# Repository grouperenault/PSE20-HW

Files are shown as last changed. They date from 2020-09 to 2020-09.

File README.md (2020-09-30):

# PSE20-HW

All the files in this directory (and its subdirectories) are subject to
the CERN-OHL-S v2 licence.

Copyright Renault SAS 2020.

This source describes Open Hardware and is licensed under the CERN-OHL-S v2.
You may redistribute and modify this documentation and make products
using it under the terms of the CERN-OHL-S v2 (https:/cern.ch/cern-ohl).

This documentation is distributed WITHOUT ANY EXPRESS OR IMPLIED
WARRANTY, INCLUDING OF MERCHANTABILITY, SATISFACTORY QUALITY
AND FITNESS FOR A PARTICULAR PURPOSE. Please see the CERN-OHL-S v2
for applicable conditions.

This repository contains the Design files for the CAD and Electronic elements of the PSE20-HW project.

For a detailed description of the ELECSYR syringe pump, please refer to [the documentation section](documentation/).

Two stacked ELECSYR units

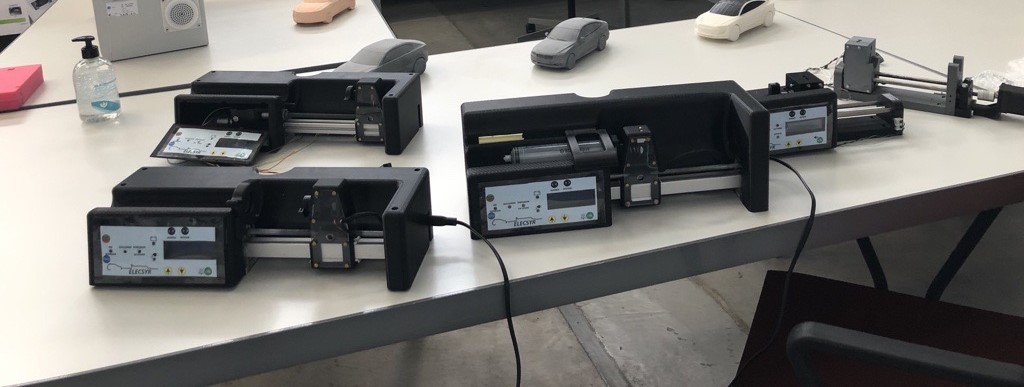
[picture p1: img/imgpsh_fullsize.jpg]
Early ELECSYR prototypes


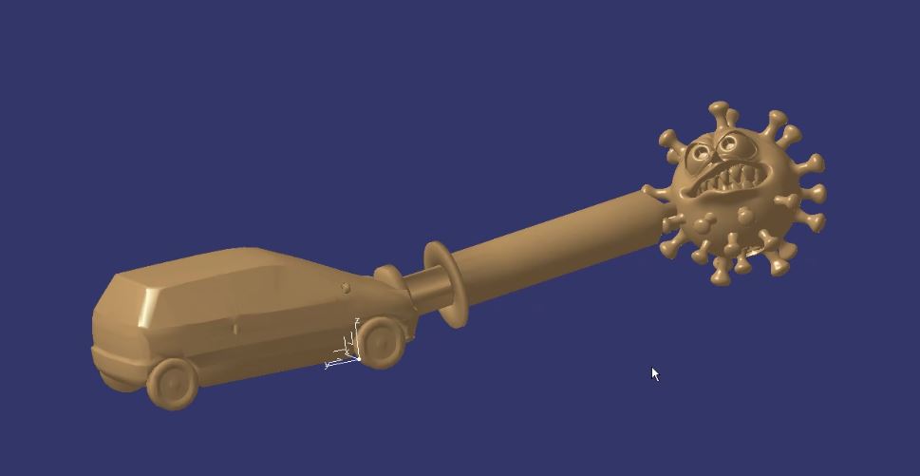
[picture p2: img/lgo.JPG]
Project Logo


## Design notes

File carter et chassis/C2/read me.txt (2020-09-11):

in this directory, you will find 3D data about C2 housing
data about other components (chassis, cutting plastic parts etc) are in C1 directory

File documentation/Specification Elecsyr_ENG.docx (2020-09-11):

Functionnal and technical description of ElecSyr, Electrical Syringe Pump

Contents

# 1. Historical

Name | Modifications | Version | Date
Sébastien LAURENT | Creation | 0.1 | 27/06/2020
Sébastien LAURENT | English translation | 0.2 | 11/08/2020

# 2. Documents

## 2.1. Generic documents

Subject | Document Name | Reference | Version
Sécurité performances pompes perfusion | Exigences particulières pour la sécurité de base et les performances essentielles des pompes et régulateurs de perfusion | IEC 60601-2 24
Sécurité & performance appareils médicaux | Exigences générales pour la sécurité de base et les performances essentielles des appareils électro-médicaux | IEC 60601-1
CEM des appareils médicaux | Exigences générales pour la sécurité de base et les performances essentielles – Norme collatérale: Perturbations électromagnétiques – Exigences et essais | IEC 60601-1-2

## 2.2. Specific documents

Subject | Document Name | Reference | Version | Comments
functional Test report | Rapport de test AGEPS | | | On demand only

# 3. Abbréviations and définitions

## 3.1. Definitions

## 3.2. Abbréviations

PSE | : | Electrical Syringe Pump (In french, Pousse Seringue Electrique)

# 4. Purpose

The purpose of this document is to describe functionality and technical points of the ElecSyr Electrical syringe pump.

## 4.1. Context

Dans le contexte de la pandémie actuelle, le pousse seringue électrique, PSE, permet d’injecter des médicaments selon plusieurs modes.

En réanimation, les patients atteints du COVID 19 nécessitent l’utilisation de 5 à 7 PSE afin de pouvoir injecter les médicaments différents.

Notre étude porte sur un PSE basique, nommé ElecSyr, permettant de répondre à l’urgence.

Ce pousse-seringues, bien que conçu pendant le pic de la pandémie, peut répondre à d’autres besoins.

Dans notre étude, nous prenons en compte les modes de fonctionnement suivant

- Continu : injection en continu d’un produit
- Bolus : injection ponctuelle à débit plus élevé. Le mode Bolus est un complément au mode continu. C’est-à-dire, que l’injection de la drogue etant en mode continu le praticien peut venir soulager le patient en lui injectant une dose plus forte ponctuellement

In the context of the current pandemic, the electric syringe pump, PSE, allows the injection of drugs in several ways.

In intensive care, patients with COVID 19 require the use of 5 to 7 PSE in order to be able to inject needed drugs.

Our study focuses on a basic PSE, called ElecSyr, to respond to the emergency.

This syringe pump, although designed during the peak of the pandemic, can meet other needs.

In our study, we take into account the following modes of operation

- Continuous injection of a product
- Bolus: a higher-flow one-off injection. The Bolus mode is a complement to the continuous mode. That is, that the injection of the drug being in continuous mode the practitioner can come to relieve the patient by injecting a higher dose punctually

# 5. global description

## 5.1. Technical features

ElecSyr is composed as folowing :

Main features are :

Built-in features | Values
Flow | Min: 1 ml/h and max 1200ml/h
Step-by-step setting | 0,1ml/h
Power
220V - 60Hz
Internal backup battery | More than 1 hour autonomy (tbc)
Mode
Continuous | Fixed flow adjusted by user
Bolus | 500ml/h for speed (this value may be change in configuration mode) Durin bolus, injected volume is shown on screen
Alert
End Course Av | LED alert - Sound - message
End Race 10% | LED alert - Sound - message
Detection Occlusion | LED alert - Sound - message
sector/battery | LED battery / LED Sector
device failure (internal check) | message - Sound
Syringes
Possible adjustments | InternalTable of 6: default BD platispak 50ml Luer Lock
Fixation
on set
onvertical colonn

## 5.2. Human Machine Interface

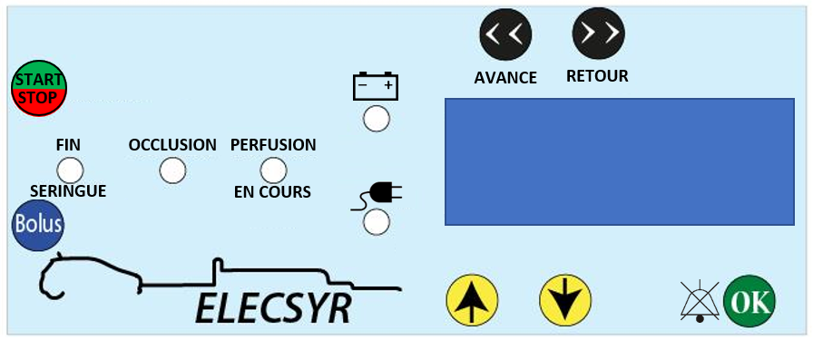
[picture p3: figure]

The HMI consists of:

- Start/stop button: used to start or stop the infusion
- Bolus button: used to launch the Bolus function
- Fast Forward button: used to move at high speed the trolley to meet the syringe
- Fast reward button: used to move in reverse speed the trolley.
- OK button: allows you to make and validate the settings (syringe choice, flow choice), to mute the sound of the alarms
- Button up: When settings it allows you to increment the flow values and choose the syringe
- Down button: When settings it allows you to decrement the flow values and choose the syringe
- Led End syringe: used to indicate 10% end of injection and end of injection
- Led Occlusion: It indicates an occlusion
- Led Perfusion in progress: green indicator indicating an infusion in progress
- Led Bat OK: Battery status indicator
- Led Sector OK: Industry Status Indicator
- A Buzzer makes sounds during different alarms
- An LCD with 2 lines – 16 characters allows you to see all the necessary information

# 6. Models

Following different tests done and exchanges with medical people, different models were developed to take into account the constraints of hospitals (stackable, waterproof, syringe fixing points), functional constraints (spring or electronic overpressure sensor) and production tools (electronic board with through-hole technology or SMD, 3D printing and cutting).

Consequently, there are 10 possible versions of ElecSyr

Assembly | Housing | mecanism | PCB | Software | Pressure sensor | comments
1 | C1 | 2 | Through hole | 1 | Spring | Checked by AGEPS
2 | C1 | 2 | Through hole | 2 | Electronic (Tyco) | Checked by AGEPS
3 | C1 | 2 | SMD | 1 | Spring | Equal to Assembly 1
4 | C1 | 2 | SMD | 2 | Electronic (Tyco) | Checked by AGEPS
5 | C2 | 2 | Through hole | 1 | Spring | Equal to Assembly 1
6 | C2 | 2 | Through hole | 2 | Electronic (Tyco) | Equal to Assembly 2
7 | C2 | 2 | SMD | 1 | Spring | Equal to Assembly 1
8 | C2 | 2 | SMD | 2 | Electronic (Tyco) | Equal to Assembly 4
9 | C3 | 2 | SMD with reduced size | 1 | Spring | Digital version only
10 | C3 | 2 | SMD with reduced size | 2 | Electronic (Tyco) | Digital version only

Housing 1 : easy to stack

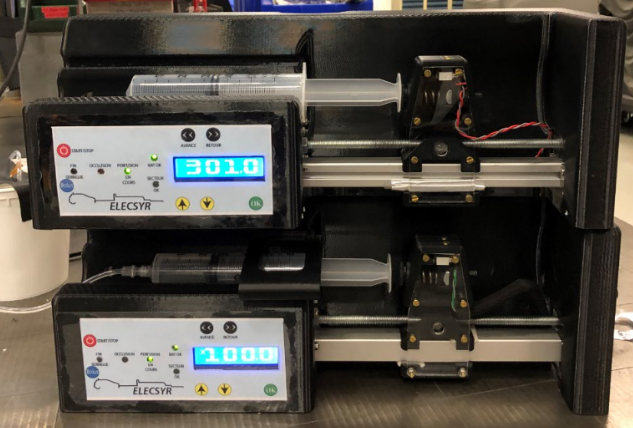
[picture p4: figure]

housing 2 : reduced height, stackable by small rods to put inside hole

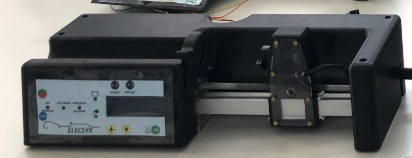
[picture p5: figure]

housing 3 : same as 2, with smaller length and width (-30mm)

Electronic board : through hole technology with Arduino board

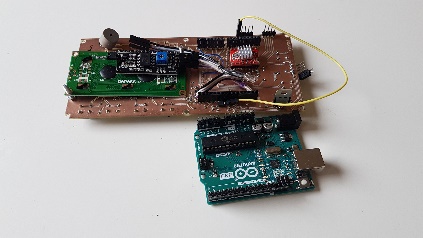
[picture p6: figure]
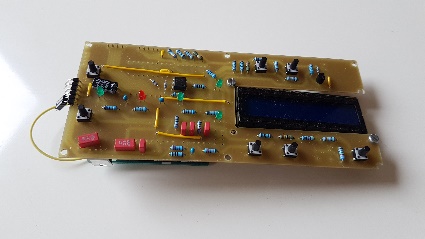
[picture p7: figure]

Electronic board: SMD technology (atmel IC is directly integrated on the board – no Arduino board)

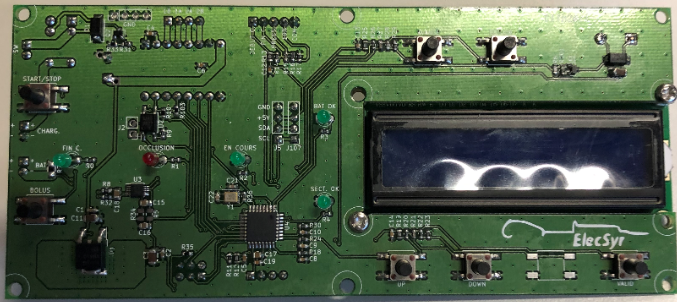
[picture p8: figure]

Spring pressure sensor

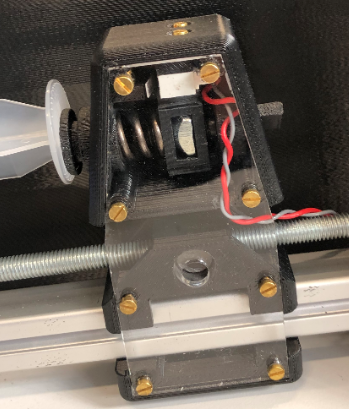
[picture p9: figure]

Electronic pressure sensor from TE Connectivty. The FX29K0-100B-0025-L was used instead of spring and mechanical detection. This systems allows to adjust with more accuracy pressure level It also helps in end of course detection and about syrnge positioning. With this sensor we are able to integrate an automatic fast positioning till syringe detection.

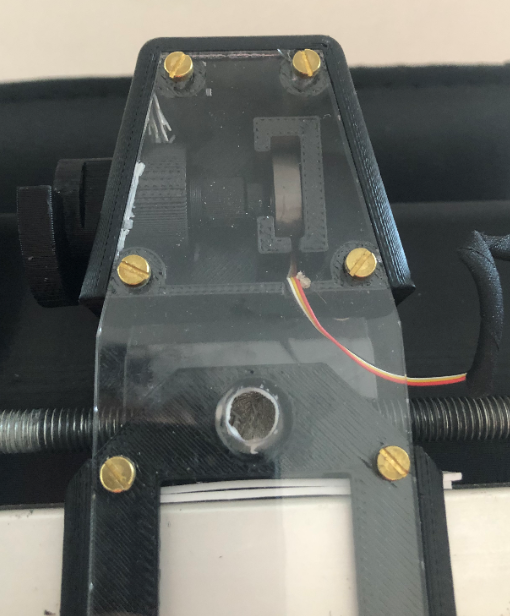
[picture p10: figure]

# 7. Functional descrption

## 7.1. State flow

## 7.2. Initialisation

When power is set on , the device starts and makes internal checks. If ok, it initiates feed monitoring and puts itself in a state of waiting.

## 7.3. Surveillance alimentation

The system checks states of main power supply and battery.

## 7.4. Etat d’attente

In that mode, you can :

- Choice and validate the syringe by using Up & Down button and OK button

Syringe 1 corresponds to the plastipak luer lock 50ml BD

- Set the flow

Flow may be adjusted by UP and DOWN buttons and each number is validated by pressing OK button

## 7.5. Distribution

Continuous:

Once the syringe and flow are validated, the Start/Stop button tap allows you to launch/stop the infusion.

At any time, if an infusion is in progress, the start/stop button stops the current infusion

Bolus :

A first push allows you to enter in Bolus function

A second continuous push launches the bolus function: the flow that appears on the screen corresponds to the additional quantity injected via the bolus function.

When the button is released, ElecSyr returns to its previous state (continuous infusion or waiting)

This mode is only available during continuous injection or waiting mode

## 7.6. Avance rapide

By pushing it, you can move quickly the trolley in direct way

If Elecsyr is equipped with an electronic pressure sensor, this function is made automatically by a push.

If Elecsyr is equipped with mechanical pressure detection, a continue push is necessary to move the trolley.

## 7.7. Retour rapide

By pushing it, you can move quickly the trolley in reverse way

Specification Elecsyr_ENG revision : 0.1 12/27 Confidential C

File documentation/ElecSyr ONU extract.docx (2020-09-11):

ElecSyr, made by Renault

# Document description

This document is an extract of project call from ONU.

ElecSyr was a candidate but didn’t win any award.

# Project description

At the start of the pandemic, a Renault team was formed to design a "basic" automatic electric syringe pump to meet the needs of hospitals. As part of the treatment of COVID, each patient requires between 5 and 7 syringe pumps. There was a high risk of supply disruption. We got closer to the nursing staff (nurse and doctors), in order to understand the basic functions of a syringe pump. ElecSyr allows continuous and / or pulsed injection of a drug by infusion. The flow rate is adjustable, min value: 2ml / h. Different types of syringes are accepted with default BD plastipak Luerlock 50ml. ElecSyr is made from simple components:

- 3D printed parts

- cut pieces

- electronic board with Arduino board (or only Atmel chip)

- Stepper motor Nema 17

ElecSyr has a cost price around 200€ without any negociation and in very small quantity. It is easy to assemble

# Added Value against COVID

ElecSyr makes it easier to manage, through automation, the administration of continuous medication. It is easily reprogrammable to add new syringe models and enrich its functionalities. ElecSyr is simple to manufacture and its cost price is very low compared to existing product on the market. Usable in the context of the current pandemic, it may subsequently be used for the treatment of other pathologies. hospitals that do not currently have a syringe pump because of the high cost, it is also an opportunity to get one.

# Innovative content of the proposal

the innovation consists of the simple, frugal realization of the electric syringe pump. it is a response to the current emergency. Its modular design makes it possible to take into account the means of production available: laser cutting, 3D printing, 3 housing solutions (stackable, reduced height, reduced bulk), 3 electronic boards depending on tools and skills (SMD or through components), spring or electronic pressure sensor ; by these choices, it is possible to assembly 10 different ElecSyr syringe pumps.

# Impact on economic, social, and environmental sustainability

- design from basic components

- Simple assembly

- simple realization

- scalable and adaptable: the software and electronics can easily be upgraded to consider current and future local needs

- repairability

- Economic

- no environmental impact

# Potential benefits for developing countries

- provide material meeting the basics of a syringe pump at a much lower cost than an existing product - ease of supply of parts, manufacturing and assembly - the software, easily upgradeable, can integrate local constraints (type of syringes, flow ranges, new features)

- simple assembly, repairable

- few components

# Development stage

3 phases of prototypes produced: - a first in 3D printing to verify the technical choices - a second integrating the constraints of the bichat hospital (Paris): waterproofing, fixing, stacking, alerts, messages for nursing staff These second prototypes were tested in hospitals in Paris (functional) - a third version integrating test feedback, more compact with SMD electronic components and electronic pressure sensor - EMC tests planned, to be carried out To do : - optimization on trolley sensor mounting. - Assembly to be finalized taking into account local functional and assembly needs (3D tool) need in terms of Manufacturing, assembly software development for update and complement. production of electronic cards

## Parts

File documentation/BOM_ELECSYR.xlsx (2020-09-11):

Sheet: SMD board
Id | Ref | Empreinte | Qté | Désignation | Fournisseur | ref
1 | R7 | R_1206_3216Metric_Shunt | 1 | 0.1R | RS | 566-058
2 | SW3A1,SW2A1,SW2B1,SW2C1,SW3C2,SW3D2,SW3B1 | SW_SPST_B3S-1000 | 7 | Switch façade | RS | 718-2459
3 | BT1,J1,SW1A101 | PinHeader_1x02_P2.54mm_Vertical | 3 | embase JST XH 2 pin | RS | 820-1554
4 | J3 | PinHeader_1x04_P2.54mm_Vertical | 1 | Pin header 4 pin | RS
5 | M1 | PinHeader_1x04_P2.54mm_Vertical | 1 | embase JST XH 4 pin | RS | 820-1551
6 | J103 | PinHeader_1x05_P2.54mm_Vertical | 1 | embase JST XH 5 pin | RS | 820-1560
7 | A2 | Pololu_Breakout-16_15.2x20.3mm | 1 | Pololu_Breakout_A4988 | Reprap
8 | C8,C10,C1,C2,C9 | C_0603_1608Metric | 5 | 47n | RS | 652-0162
9 | R18,R30,R24 | C_0603_1608Metric | 3 | 22k | RS | 679-0005
10 | C6,C4,C5,C12,C13,C14,C19 | C_0603_1608Metric | 7 | 100n | RS | 133-5658
11 | U1 | TO-252-2 | 1 | NCP1117-1.5_TO252 | RS | 516-5871
12 | U2 | SO-4_4.4x3.6mm_P2.54mm | 1 | LTV-357T | RS | 691-2088
13 | REF** | LCD1602_2 | 1 | LCD 16x02 I2C | amazon | https://www.amazon.fr/gp/product/B07PGZ9B51/ref=ppx_yo_dt_b_asin_title_o03_s01?ie=UTF8&psc=1
14 | D4,D6,D9,D10 | LED_D3.0mm | 4 | Led VERTE | RS | 180-8502
15 | D5 | LED_D3.0mm | 1 | Led ROUGE | RS | 178-0909
16 | R0,R1,R2,R3,R4,R9 | R_0603_1608Metric | 6 | 680 | RS | 820-6887
17 | R6,R11,R31 | R_0603_1608Metric | 3 | 2.2k | RS | 820-6824
18 | R12,R13,R19,R25 | R_0603_1608Metric | 4 | 1k | RS | 223-0427
19 | R8,R14,R20,R26,R32 | R_0603_1608Metric | 5 | 249 | RS | 679-0037
20 | R15,R21,R27 | R_0603_1608Metric | 3 | 412 | RS | 122-8862
21 | R16,R22,R28 | R_0603_1608Metric | 3 | 825 | RS | 679-0728
22 | R17,R23,R29 | R_0603_1608Metric | 3 | 2490 | RS | 679-0147
23 | Q1,Q2 | SOT-23 | 2 | BC817 | RS | 216-9410
24 | C3,C11,C23 | C_1206_3216Metric | 3 | 10u | RS | 802-9977
25 | R10,R101,R103,R33,R35 | R_0603_1608Metric | 5 | 10k | RS | 678-9667
26 | LS1 | Buzzer_12x9.5RM7.6 | 1 | Buzzer | RS | 771-6967
27 | D2,D1 | D_SMA | 2 | S1G | RS | 761-3723
28 | C7 | CP_Radial_D10.0mm_P5.00mm_P7.50mm_H16mm | 1 | 470u | RS | 315-0574
29 | C15,C16,C17,C18 | C_0805_2012Metric | 4 | 1u | RS | 133-5653
30 | C21,C22 | C_0603_1608Metric | 2 | 12p (value depend of Y1) | RS | 652-0926
31 | J4 | PinHeader_2x03_P2.54mm_Vertical | 1 | ICSP | RS
32 | K1 | Relay_SPDT_Omron_G5V-1 | 1 | G5V-1 9 | RS | 683-9255
33 | R5,R34 | R_0805_2012Metric | 2 | MMZ2012Y152B | RS | 604-2022
34 | R36 | R_0603_1608Metric | 1 | 1M | RS | 213-2676
35 | U3 | TSSOP-10_3x3mm_P0.5mm | 1 | ADS1115IDGS | RS | 709-4544
36 | U4 | TQFP-32_7x7mm_P0.8mm | 1 | ATMega328P-AU | RS | 131-0271
37 | Y1 | Crystal_SMD_3225-4Pin_3.2x2.5mm | 1 | 16MHz | RS | 775-3736
38 |  |  | 1 | Porte clip JST XH 5 pin | RS | 820-1627
39 |  |  | 1 | Porte clip JST XH 4 pin | RS | 820-1618
40 |  |  | 3 | Porte clip JST XH 2 pin | RS | 820-1611
41 |  |  | 15 | Clip JST XH | RS | 820-1529
44 |  |  | 1 | microrupteur ss lamelle | RS | 804-6253
45 |  |  | 2 | microrupteur lamelle | RS | 804-6262

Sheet: Mechanical parts
ss éléments |  | nombre
Chariot | chariot inférieur | 1 | 3D
 | patins teflon | 2
 | ecrou tranversal M8 | 1
 | chariot supérieur | 1 | 3D
 | pousse-piston | 1 | 3D
 | escargot piston | 1 | 3D
 | axe maintien escargot | 1
 | plaque latérale | 2
 | tige appui micro switch | 1
 | vis appui patin M2*8 | 4
 | vis M3*36 | 8
 | ecrou M3 | 8
 | rondelle plate M3 | 8
Mécanisme | profilé alu 20*20*250 | 1
 | roulement 608ZZ | 1 | reprap
 | tige filetée M8 | 1
 | support moteur | 1 | 3D
 | coupleur 5mm*8mm | 1 | reprap
 | moteur Nema 17 0,48Nm | 1 | reprap
extérieur | carter | 1
 | support facade | 1
 | vis fixation façade M2 *5 | 6
 | vis fixation carter M2*8 | 10
chassis | socle | 1
 | support mecanisme G | 1
 | support mecanisme D | 1
 | flasque arret roulement | 1
 | flasque maintien chargeur | 2
 | Arret X chargeur | 1
 | flasque maintien batterie | 2

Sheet: EE parts
 |  |  | Supplier | Reference
 | PCB CMS | 1 | CIF
 | A4988 - Pilote de moteur pas à pas Stepstick | 1 | reprap
 | Câble pour NEMA 17 de 20cm | 1 | reprap
 | Nema 17 | 1 | reprap
 | ventilateur (Not used) | 0 | reprap
 | coupleur 5*8 | 1 | reprap
 | LCD 2*16 | 1 | ?
cablage | cablage interne |  | internal team
 | Chargeur de batterie Mascot Pack batterie Lithium-Ion | 1 | RS | 463-1181
 | Bloc batterie rechargeable Ansmann Lithium-Ion 7.4V 2.6Ah x 2 | 1 | RS | 776-0857
 | cable secteur | 1 | RS | 873-0709
 | Interrupteur à bascule Rouge bipolaire On-Off lumineux IP44 | 1 | RS | 377-9759
 | Electronic pressure sensor | 1 | TE connectivity | FX 29

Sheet: through hole board
Id | Référence | Boitier | Quantité | Désignation | Fournisseur | ref
1 | A2 | Pololu_Breakout-16_15.2x20.3mm | 1 | Pololu_Breakout_A4988 | Amazon/
2 | U1 | TO-220-3_Vertical | 1 | LM7805_TO220 | RS | 298-8508
3 | U2 | DIP-6_W7.62mm | 1 | 4N35 | RS | 699-8155
4 | D4 | LED_D3.0mm | 1 | Fin_course VERTE | RS | 180-8502
5 | D5 | LED_D3.0mm | 1 | Occlusion ROUGE | RS | 178-0909
6 | D6 | LED_D3.0mm | 1 | PERF EN COURS VERT | RS | 180-8502
7 | D9 | LED_D3.0mm | 1 | BAT OK ROUGE | RS | 178-0909
8 | D10,D11 | LED_D3.0mm | 2 | LED verte | RS | 180-8502
9 | SW2A1 | SW_PUSH_6mm_H9.5mm | 1 | UP | RS | 479-1435
10 | SW2B1 | SW_PUSH_6mm_H9.5mm | 1 | DOWN | RS | 479-1435
11 | SW2C1 | SW_PUSH_6mm_H9.5mm | 1 | VALID | RS | 479-1435
12 | SW3A1 | SW_PUSH_6mm_H9.5mm | 1 | StartStop | RS | 479-1435
13 | SW3B1 | SW_PUSH_6mm_H9.5mm | 1 | BOLUS | RS | 479-1435
14 | SW2D1 | SW_PUSH_6mm_H9.5mm | 1 | Avance | RS | 479-1435
15 | SW3C2 | SW_PUSH_6mm_H9.5mm | 1 | RETOUR | RS | 479-1435
16 | SW3D2 | SW_PUSH_6mm_H9.5mm | 1 | RESERVE1 | RS | 479-1435
17 | Q1 | TO-92 | 1 | BC337 | RS | 671-1116
18 | A1 | Arduino_UNO_R3 | 1 | Arduino_UNO_R3 | RS | 715-4081
19 | R0,R1,R2,R3,R4,R6,R8 | R_Axial_DIN0204_L3.6mm_D1.6mm_P5.08mm_Horizontal | 7 | 680 | RS | 506-5024
20 | R5 | R_Axial_DIN0204_L3.6mm_D1.6mm_P5.08mm_Horizontal | 1 | 100 | RS | 477-7681
21 | R7,R10,R101 | R_Axial_DIN0204_L3.6mm_D1.6mm_P5.08mm_Horizontal | 3 | 10k | RS | 491-1645
22 | R9 | R_Axial_DIN0204_L3.6mm_D1.6mm_P5.08mm_Horizontal | 1 | 300 | RS | 683-4196
23 | R11 | R_Axial_DIN0204_L3.6mm_D1.6mm_P5.08mm_Horizontal | 1 | 2.2k | RS | 506-5096
24 | R12 | R_Axial_DIN0204_L3.6mm_D1.6mm_P5.08mm_Horizontal | 1 | 1k | RS | 683-3165
25 | R13,R19,R25 | R_Axial_DIN0204_L3.6mm_D1.6mm_P5.08mm_Horizontal | 3 | 1ko | RS | 683-3165
26 | R14,R20,R26 | R_Axial_DIN0204_L3.6mm_D1.6mm_P5.08mm_Horizontal | 3 | 249 | RS | 477-7798
27 | R15,R21,R27 | R_Axial_DIN0204_L3.6mm_D1.6mm_P5.08mm_Horizontal | 3 | 412 | RS | 683-3682
28 | R16,R22,R28 | R_Axial_DIN0204_L3.6mm_D1.6mm_P5.08mm_Horizontal | 3 | 825 | RS | 477-7912
29 | R17,R23,R29 | R_Axial_DIN0204_L3.6mm_D1.6mm_P5.08mm_Horizontal | 3 | 2490 | RS | 477-8038
30 | R18,R24,R30 | R_Axial_DIN0204_L3.6mm_D1.6mm_P5.08mm_Horizontal | 3 | 22k | RS | 506-5349
31 | R102 | R_Axial_DIN0204_L3.6mm_D1.6mm_P5.08mm_Horizontal | 1 | 1M | RS | 477-8662
32 | BT1 | PinHeader_1x02_P2.54mm_Vertical | 1 | Battery_Cell | RS | 251-8086
33 | J1 | PinHeader_1x02_P2.54mm_Vertical | 1 | Entree_chargeur | RS | 251-8086
34 | J5,depart masse,moteur pàp | PinHeader_1x04_P2.54mm_Vertical | 2 | Ecran_I2C | RS | 251-8115
35 | J103, | PinHeader_1x05_P2.54mm_Vertical | 2 | Conn_01x05_Male | RS | 251-8121
36 | J107 | PinHeader_1x04_P2.54mm_Vertical | 1 | Pression_I2C | RS | 251-8115
37 | LS1 | PinHeader_1x02_P2.54mm_Vertical | 1 | Speaker | RS | 251-8086
38 | C1,C3 | C_Disc_D3.0mm_W2.0mm_P2.50mm | 3 | 470n | RS | 118-016
39 | C4,C5,C6 | C_Disc_D3.0mm_W2.0mm_P2.50mm | 3 | 100n | RS | 115-023
40 | C7 | CP_Radial_D4.0mm_P2.00mm | 1 | 100u | RS | 711-1090
41 | C2,C8,C9,C10 | C_Disc_D3.0mm_W2.0mm_P2.50mm | 3 | 47n | RS | 115-001
42 | J2 | PinHeader_1x02_P2.54mm_Vertical | 1 | shunt Opto | RS | 251-8086
43 | J4 | PinHeader_1x02_P2.54mm_Vertical | 1 | shunt 5V Arduino | RS | 251-8086
44 |  | carte cuivre nu 160*100*1,6 | 1 |  | RS | 219-2123
 |  | Chargeur batterie | 1 |  | RS | 463-1181
 |  | Batterie | 1 |  | RS | 776-0857
 |  | HP (speaker) | 1 |  | RS | 771-6982
 |  | Ecran_I2C | 1 |  | Amazon/
 |  | Stepper Nema17 - 1,7A - 0.45Nm | 1 | 1.8° | RS | 535-0489
 |  | switch fin de course | 1 |  | RS | 804-6262
 |  | switch début de course | 1 |  | RS | 804-6262
 |  | switch reste 10% | 1 |  | RS | 804-6253
 |  | switch occlusion | 1 |  | RS | 804-6262
 |  | inter On/Off | 1 |  | RS | 377-9759
 |  | gaine thermo | 1 |  | RS | 700-4620
 |  | pin header femelle pour raccord | 1 |  | RS | 251-8171
 |  | pin header male/male | 4 |  | RS | 251-8339
 |  | pin header femelle pour raccord | 4 |  | RS | 251-8171
 |  | fraise 0,1mm | 5 |  | RS | 382-002
 |  | MANQUE COUPLEUR 4*8
 |  | MANQUE VIS
COMPLEMENT ACHAT 09/04/2020
 |  | LED_D3.0mm | 1 | PERF EN COURS VERT | RS | 180-8502
 |  | C_Disc_D3.0mm_W2.0mm_P2.50mm |  | 470n | RS | 118-016
 |  | C_Disc_D3.0mm_W2.0mm_P2.50mm | 3 | 100n | RS | 115-023
 |  | SW_PUSH_6mm_H9.5mm | 1 | UP | RS | 479-1435
 |  | cordon 220 |  |  |  | 873-0709
 |  | header femelle |  |  |  | 230-4893
 |  | buzzer |  |  |  | 771-6967

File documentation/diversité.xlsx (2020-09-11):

Assemblé | Carter | Mécanique | Carte | Soft | capteur de pression | commentaire | Carter 1
1 | C1 | 2 | trav | 1 | ressort | testé par l'AGEPS
2 | C1 | 2 | trav | 2 | Tyco | testé par l'AGEPS
3 | C1 | 2 | CMS | 1 | ressort | idem Assemblé 1
4 | C1 | 2 | CMS | 2 | Tyco | testé par l'AGEPS
5 | C2 | 2 | trav | 1 | ressort | idem Assemblé 1
6 | C2 | 2 | trav | 2 | Tyco | idem Assemblé 2
7 | C2 | 2 | CMS | 1 | ressort | Idem Assemblé 1
8 | C2 | 2 | CMS | 2 | Tyco | idem Assemblé 4 | Carter 2
9 | C3 | 2 | CMS réduit | 1 | ressort | version numérique seulement
10 | C3 | 2 | CMS réduit | 2 | Tyco | version numérique seulement
 |  |  |  |  |  |  | Carter 3
 |  |  |  |  |  |  | réduit

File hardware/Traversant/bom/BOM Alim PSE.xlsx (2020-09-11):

Id | Reference | Empreinte | Qte | Valeur | Fournisseur | Ref fournisseur | N'existe pas dans la BOM de la carte on a pas de stock
1 | U1 | PinHeader_1x10_P2.54mm_Vertical | 1 | ADS1115IDGS | Amazone | https://www.amazon.fr/AZDelivery-ADS1115-Parent-3X/dp/B07QHWLTTS?__mk_fr_FR=%C3%85M%C3%85%C5%BD%C3%95%C3%91&s=computers
2 | C1 | CP_Radial_D10.0mm_P5.00mm_P7.50mm | 1 | 470u | RS | 315-0574
3 | C2 | C_Disc_D5.1mm_W3.2mm_P5.00mm | 1 | 1u | RS | 811-8364
4 | R1,R3 | R_Axial_DIN0207_L6.3mm_D2.5mm_P7.62mm_Horizontal | 2 | 249 | RS | 477-7798
5 | R5 | R_Axial_DIN0207_L6.3mm_D2.5mm_P7.62mm_Horizontal | 1 | 10k | RS | 491-1645
6 | R4 | R_Axial_DIN0207_L6.3mm_D2.5mm_P7.62mm_Horizontal | 1 | 2.2k | RS | 506-5096
7 | D1 | D_DO-41_SOD81_P7.62mm_Horizontal | 1 | D | RS | 628-9029
8 | K1 | Relay_SPDT_Omron_G5V-1 | 1 | G5V-1 | RS | 683-9255
9 | J2 | PinHeader_1x06_P2.54mm_Vertical | 1 | CONNECTEUR CARTE PSE
10 | J1 | PinHeader_1x06_P2.54mm_Vertical | 1 | CONNECTEUR ENTREE
11 | R2 | R_Axial_DIN0207_L6.3mm_D2.5mm_P7.62mm_Horizontal | 1 | 100mR | RS | 174-2721
12 | Q1 | TO-92_Inline_Wide | 1 | BC337 | RS | 671-1116

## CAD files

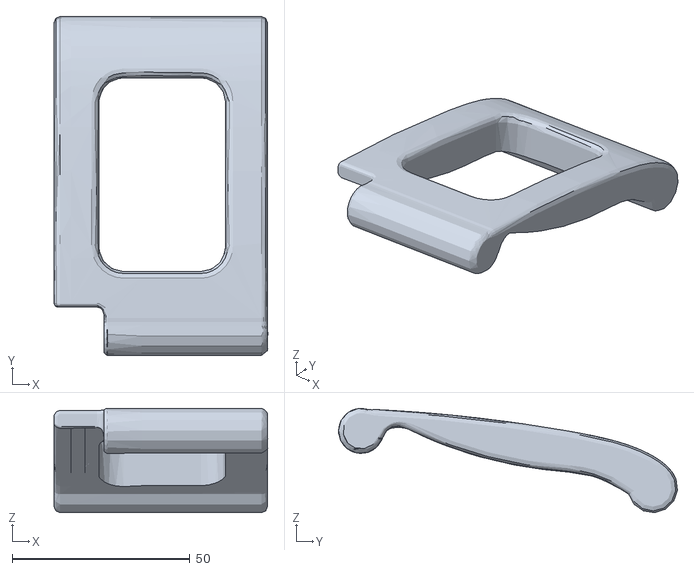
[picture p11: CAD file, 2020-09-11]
carter et chassis/C1/impression 3D/modif maintien corps seringue.stl
60.1 x 95.3 x 29.3

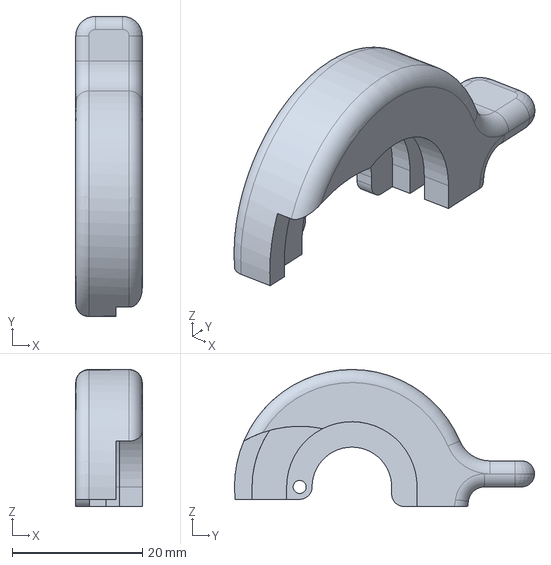
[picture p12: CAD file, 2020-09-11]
carter et chassis/trolley/chariot-switch/impression-3D/maintien-seringue.stp
10.2 x 46.0 x 21.0 mm

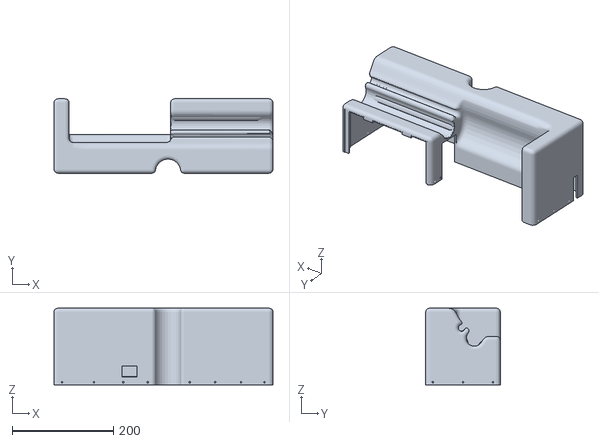
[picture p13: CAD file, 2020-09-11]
carter et chassis/C1/impression 3D/modif carter.stl
432.0 x 147.0 x 151.0

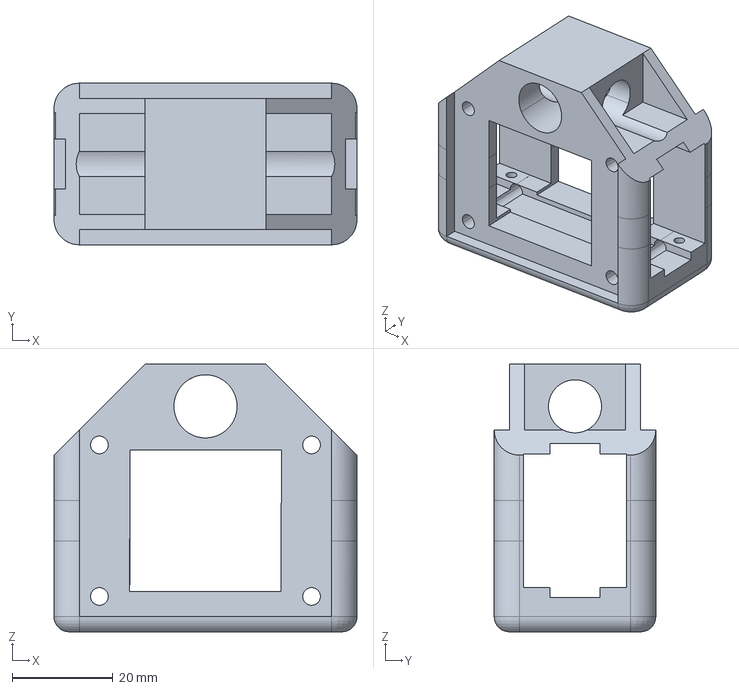
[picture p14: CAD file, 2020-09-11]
carter et chassis/C2/Fichier pour imprimante 3D/chariot-inf.stp
60.0 x 32.0 x 53.0 mm

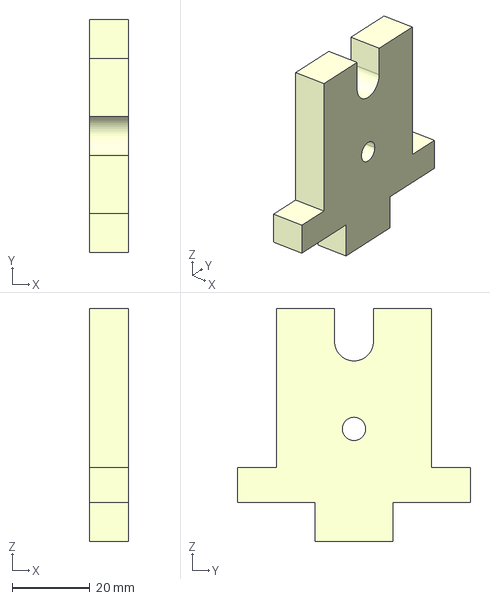
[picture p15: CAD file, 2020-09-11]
carter et chassis/C3/Palier-ar.stp
10.0 x 60.0 x 60.0 mm

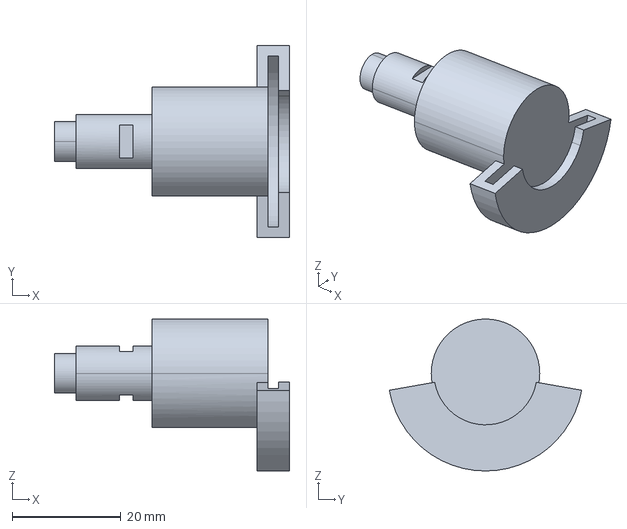
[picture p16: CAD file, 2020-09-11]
carter et chassis/trolley/chariot-capteur-force/impression-3D/appui-seringue.stp
43.3 x 35.5 x 28.0 mm

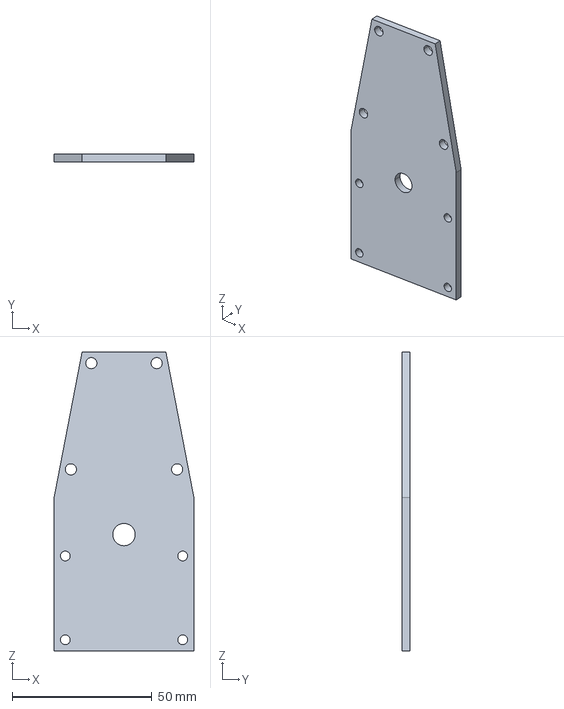
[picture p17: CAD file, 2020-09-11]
carter et chassis/trolley/chariot-switch/decoupe-laser/decoupe 3mm/plaque-fermeture.stp
50.0 x 3.00 x 107.0 mm

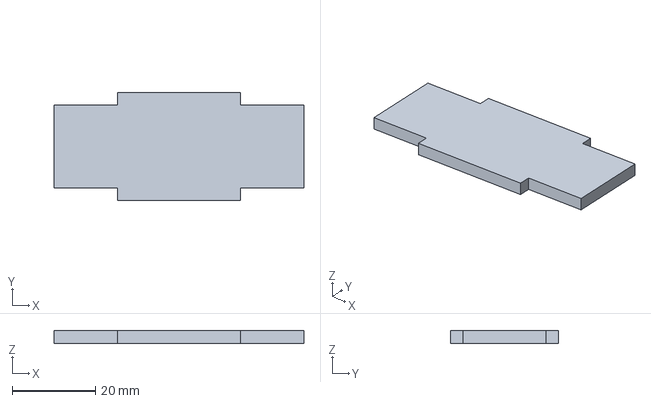
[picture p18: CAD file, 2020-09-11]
carter et chassis/trolley/chariot-switch/decoupe-laser/PTFE/plaque-teflon.stp
60.0 x 26.0 x 3.00 mm

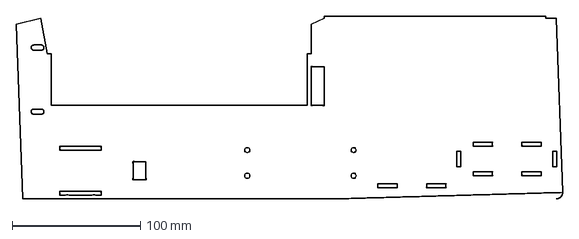
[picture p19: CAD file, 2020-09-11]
carter et chassis/C1/decoupe 10 mm/modif-socle.dxf
426.0 x 142.5 mm

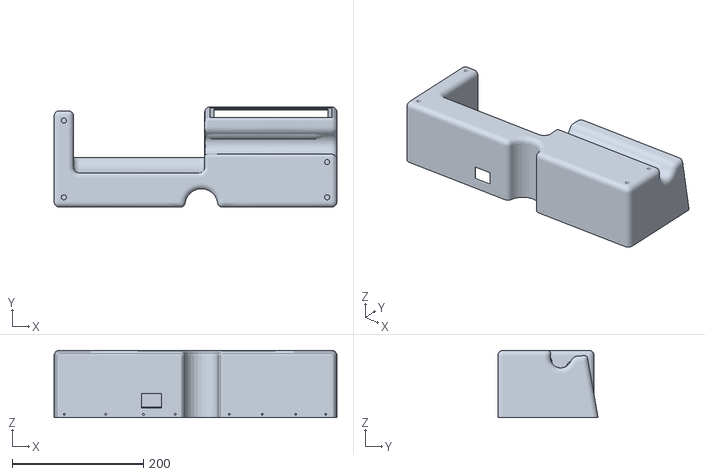
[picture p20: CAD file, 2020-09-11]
carter et chassis/C2/Fichier pour imprimante 3D/Carter-modif-hauteur.stl
432.0 x 153.0 x 102.8

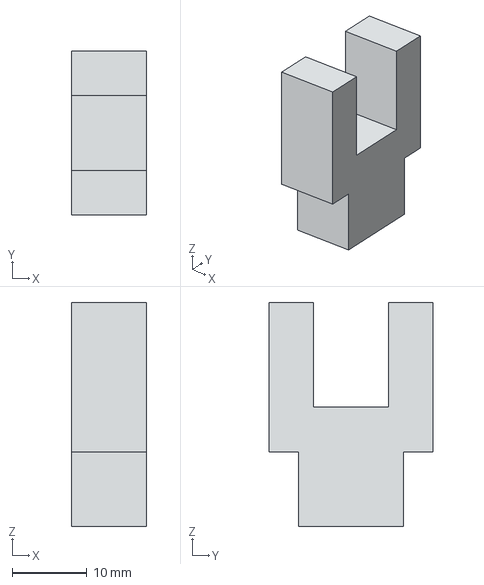
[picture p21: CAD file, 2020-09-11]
carter et chassis/C3/Arret-chargeur.stp
10.0 x 22.0 x 30.0 mm

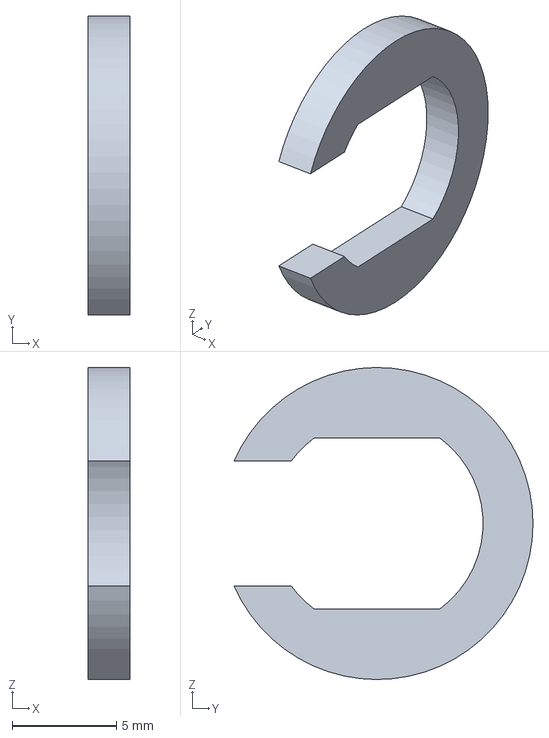
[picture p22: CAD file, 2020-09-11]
carter et chassis/trolley/chariot-capteur-force/impression-3D/clip.stp
2.00 x 14.4 x 15.0 mm

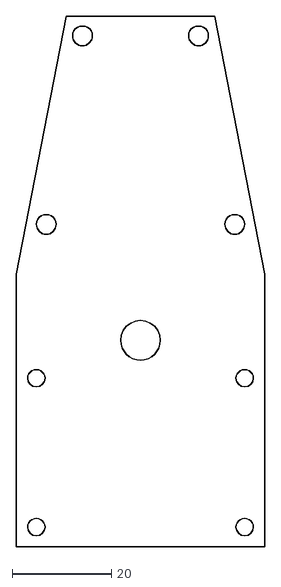
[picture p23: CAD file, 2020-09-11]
carter et chassis/trolley/chariot-switch/decoupe-laser/decoupe 3mm/plaque de fermeture.dxf
50.0 x 107.0

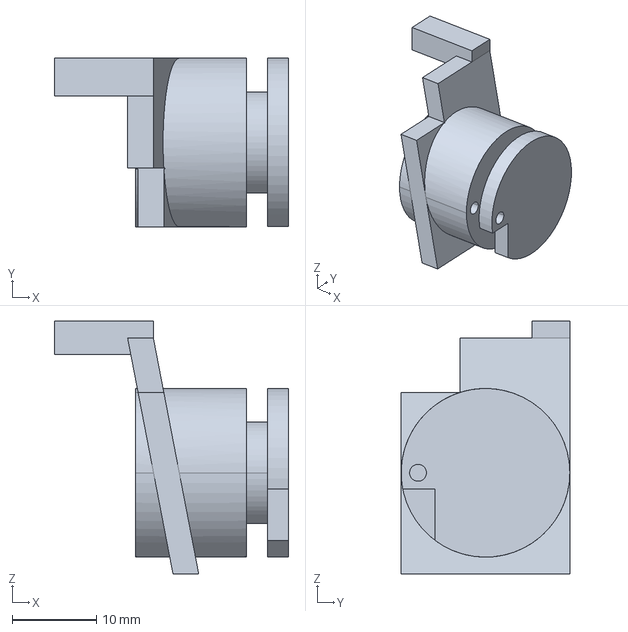
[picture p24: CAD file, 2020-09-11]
carter et chassis/trolley/chariot-switch/impression-3D/appui-seringue.stp
27.8 x 20.0 x 30.0 mm

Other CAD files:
carter et chassis/C1/decoupe 10 mm/Palier-ar-lignes.dxf
carter et chassis/C1/impression 3D/support moteur version 3D.stl
carter et chassis/C2/Fichier pour imprimante 3D/escargot.stl
carter et chassis/C2/Fichier pour imprimante 3D/appui-serringue-escargot.stl
carter et chassis/C2/Fichier pour imprimante 3D/appui-serringue-rainure.stl
carter et chassis/C2/Fichier pour imprimante 3D/chariot-inf.stl
carter et chassis/C2/Fichier pour imprimante 3D/clip.stl
carter et chassis/C2/Fichier pour imprimante 3D/corps-chariot.stl
carter et chassis/C2/Fichier pour imprimante 3D/escagot-serringue.stl
carter et chassis/C2/Fichier pour imprimante 3D/facade.stl
carter et chassis/C2/Fichier pour imprimante 3D/support-escargot.stl
carter et chassis/C2/Fichier pour imprimante 3D/support-moteur.stl
carter et chassis/C2/Fichier pour imprimante 3D/tube.stl
carter et chassis/C3/Arret-X.stl
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

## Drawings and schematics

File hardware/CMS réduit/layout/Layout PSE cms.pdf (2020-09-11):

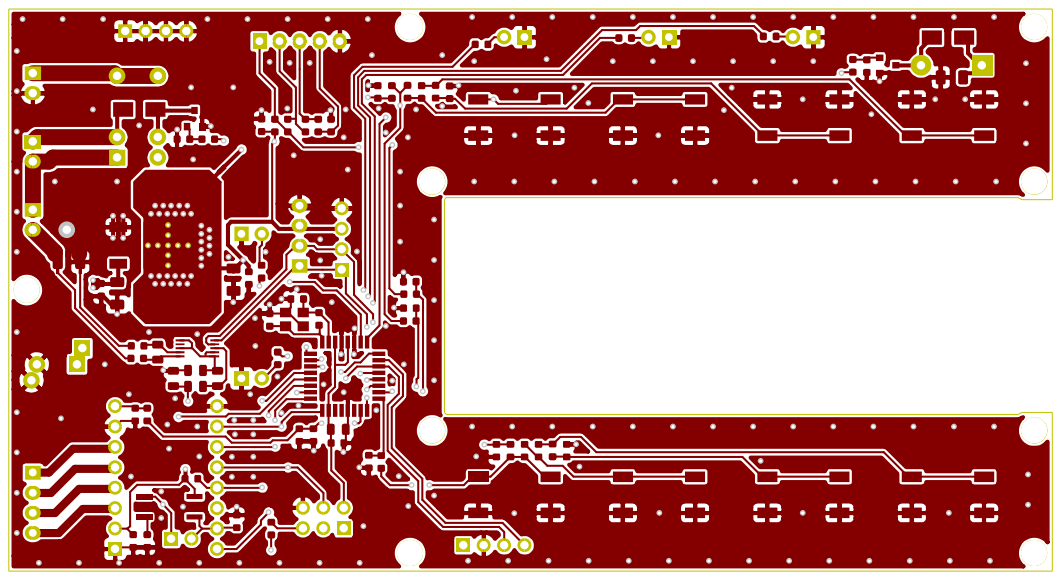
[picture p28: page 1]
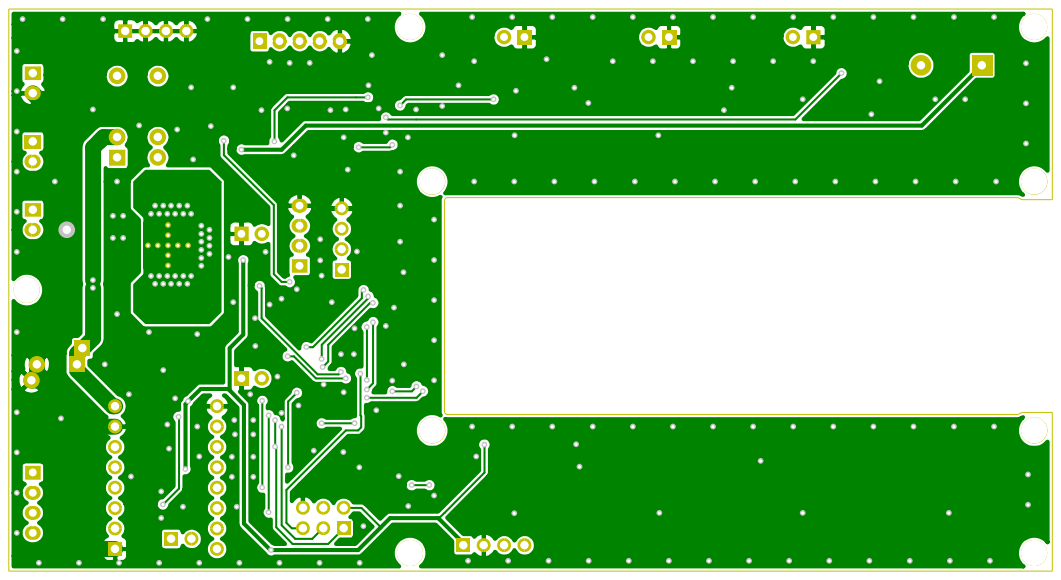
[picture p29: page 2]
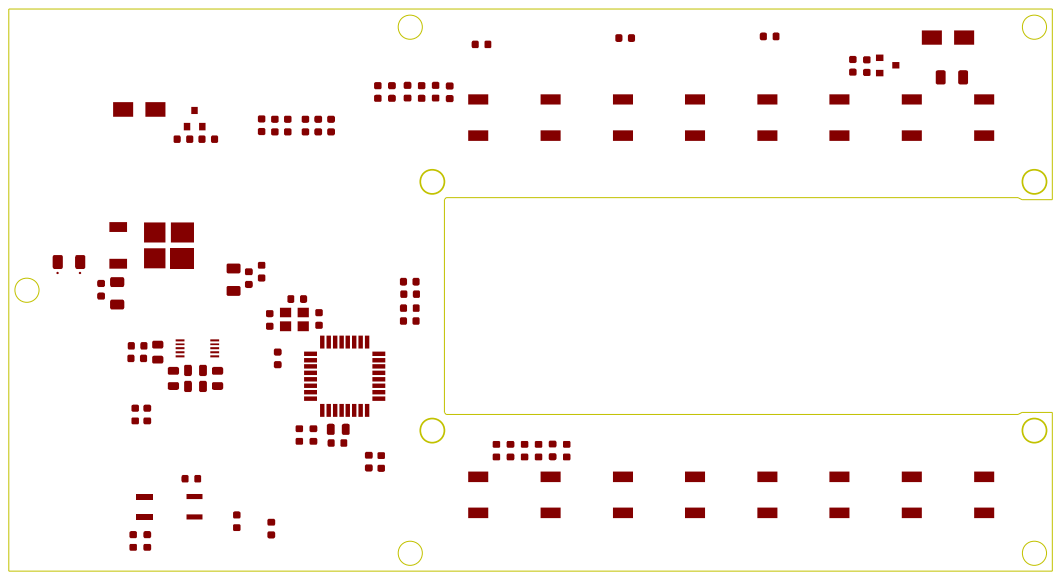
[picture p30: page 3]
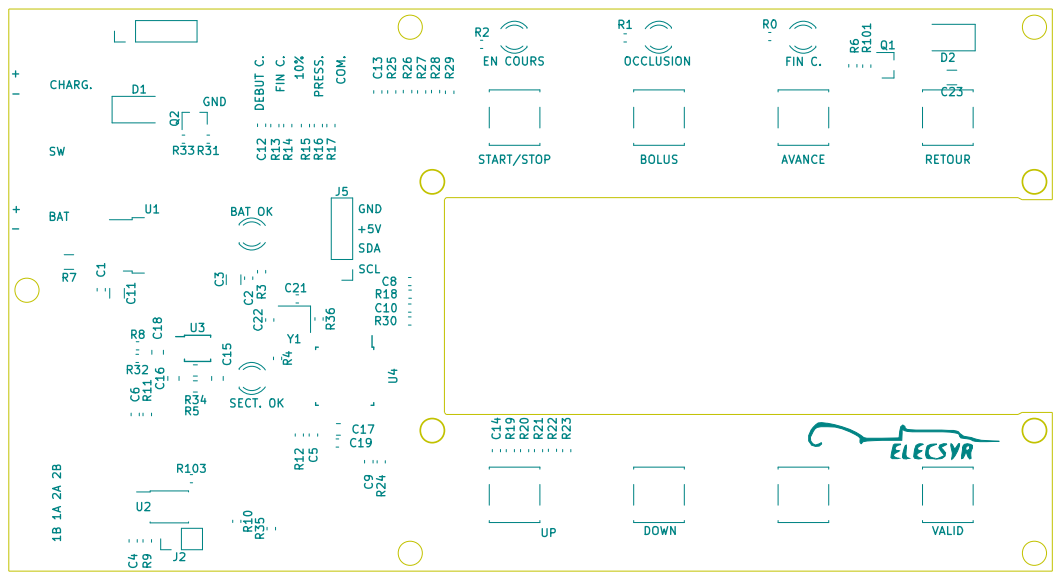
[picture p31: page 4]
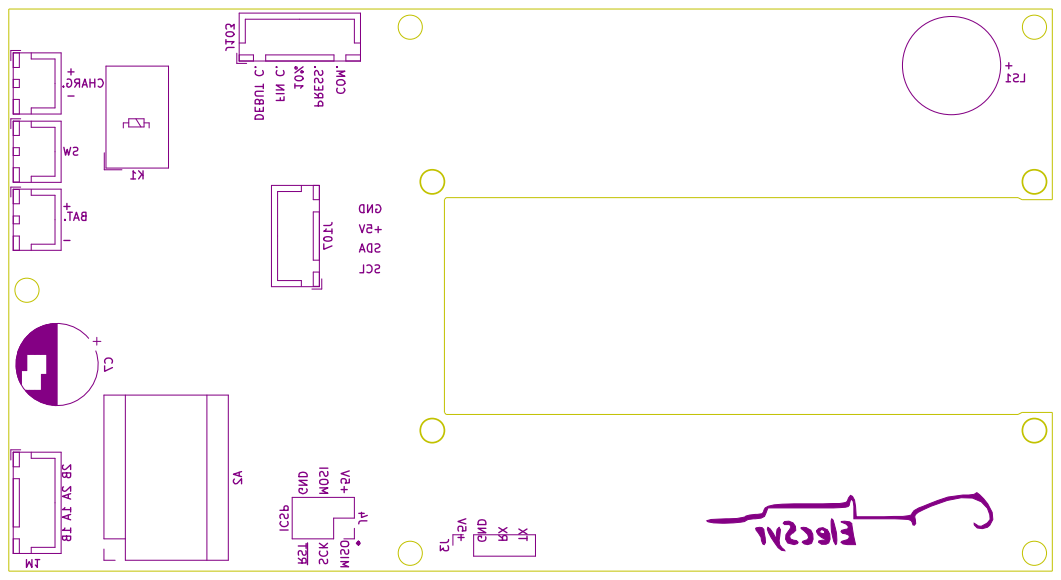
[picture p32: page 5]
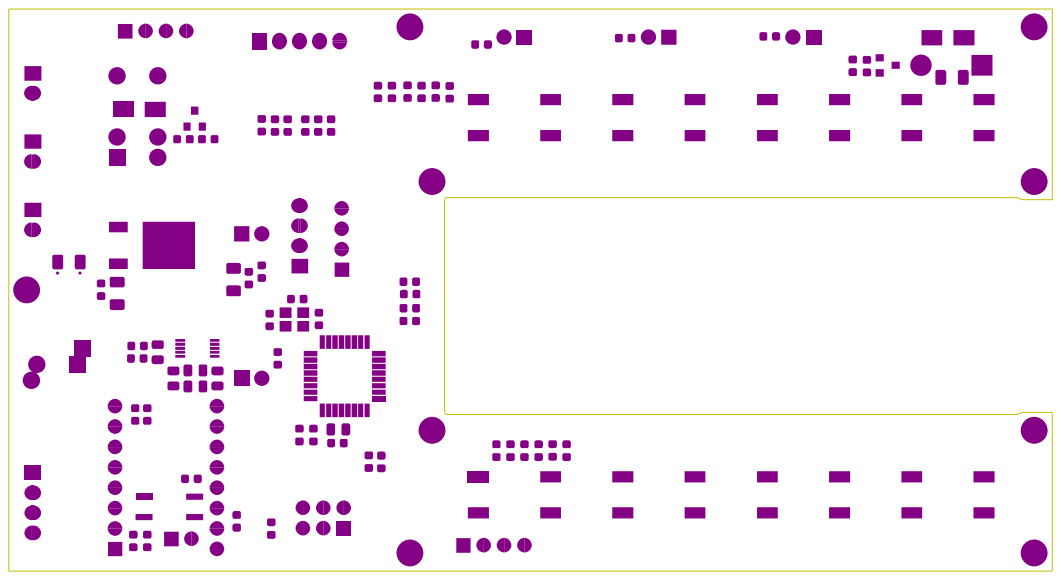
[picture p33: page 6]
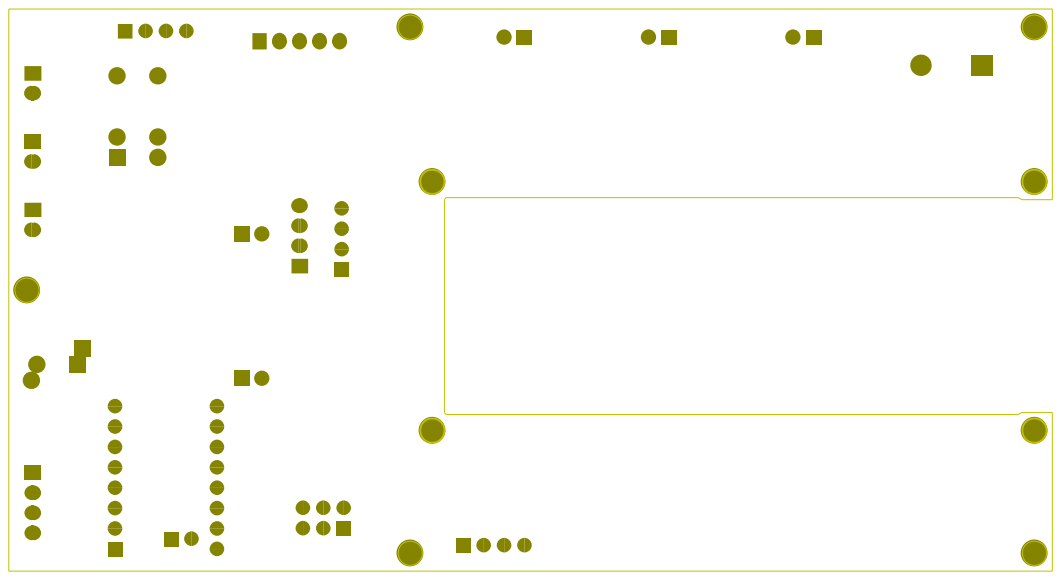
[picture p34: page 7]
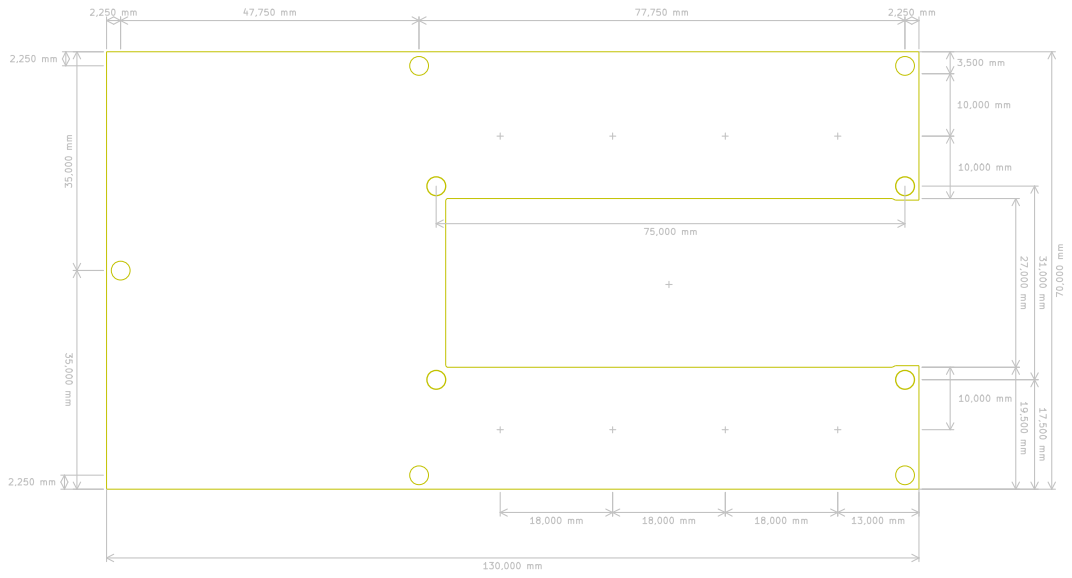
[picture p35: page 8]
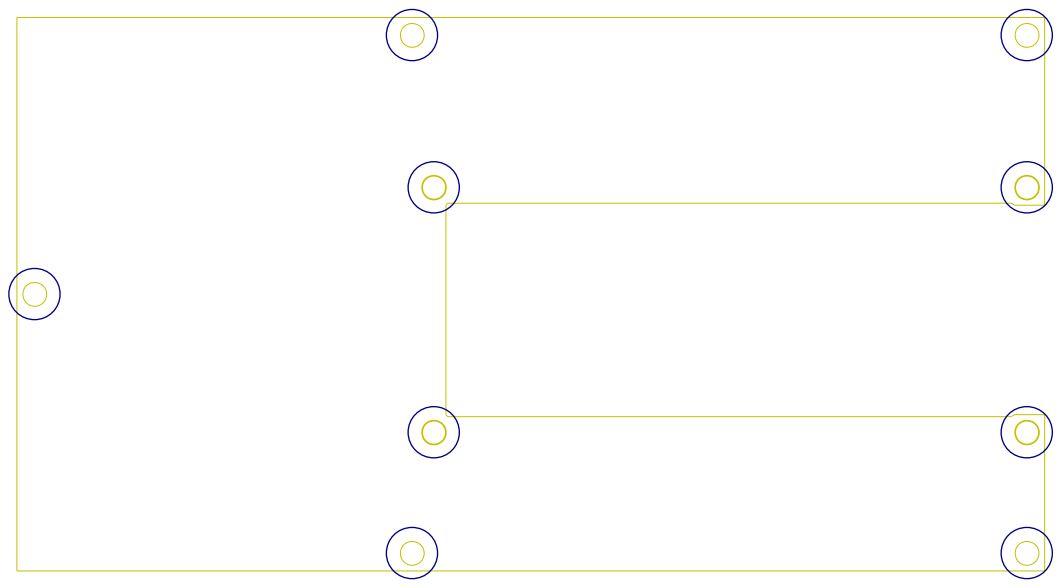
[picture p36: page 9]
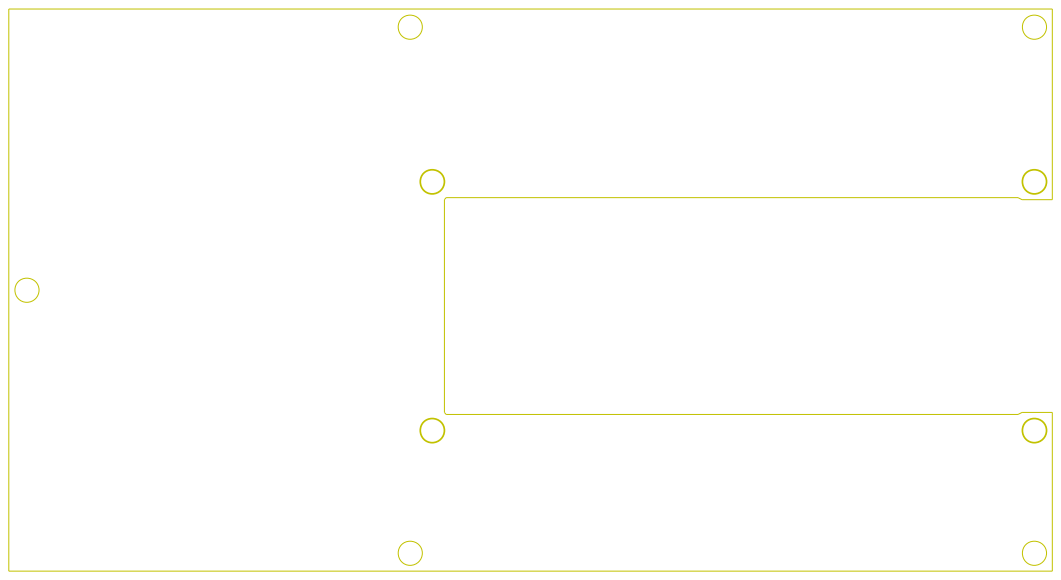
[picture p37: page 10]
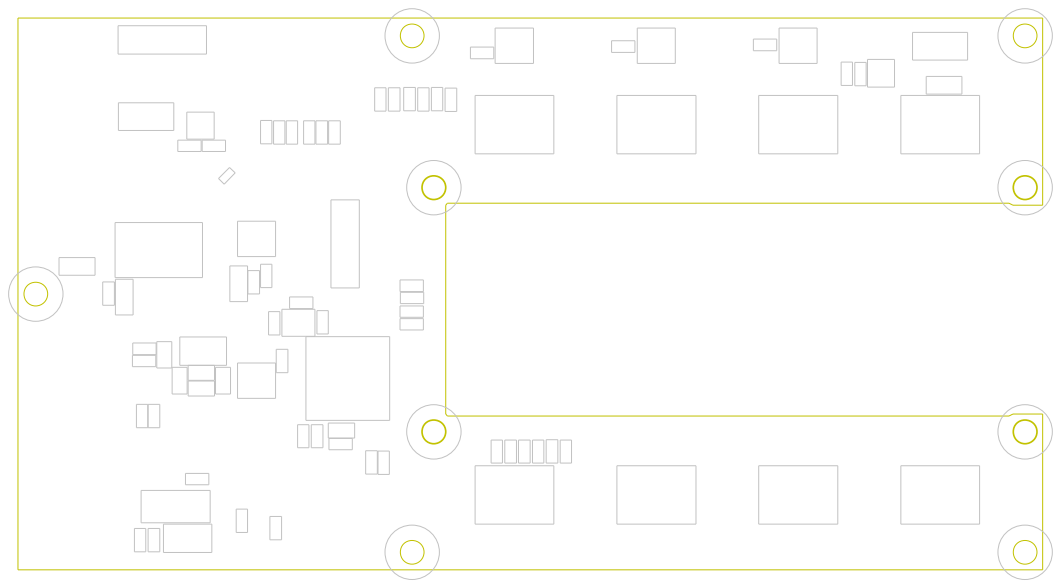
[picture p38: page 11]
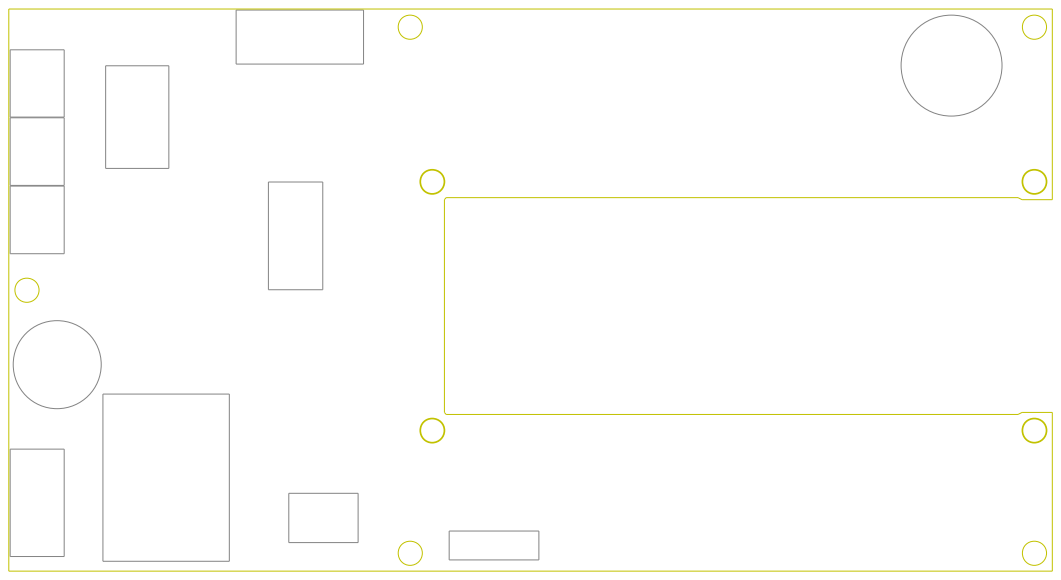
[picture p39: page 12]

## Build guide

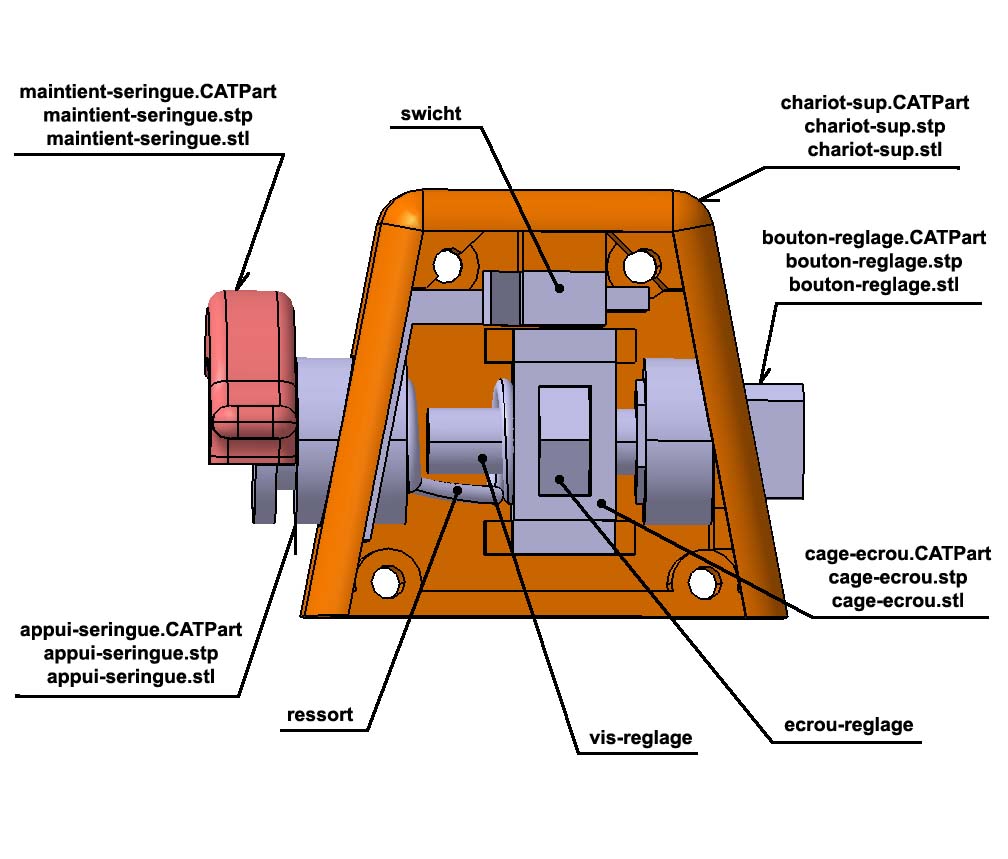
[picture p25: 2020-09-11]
carter et chassis/trolley/chariot-switch/assemblage-sup.jpg

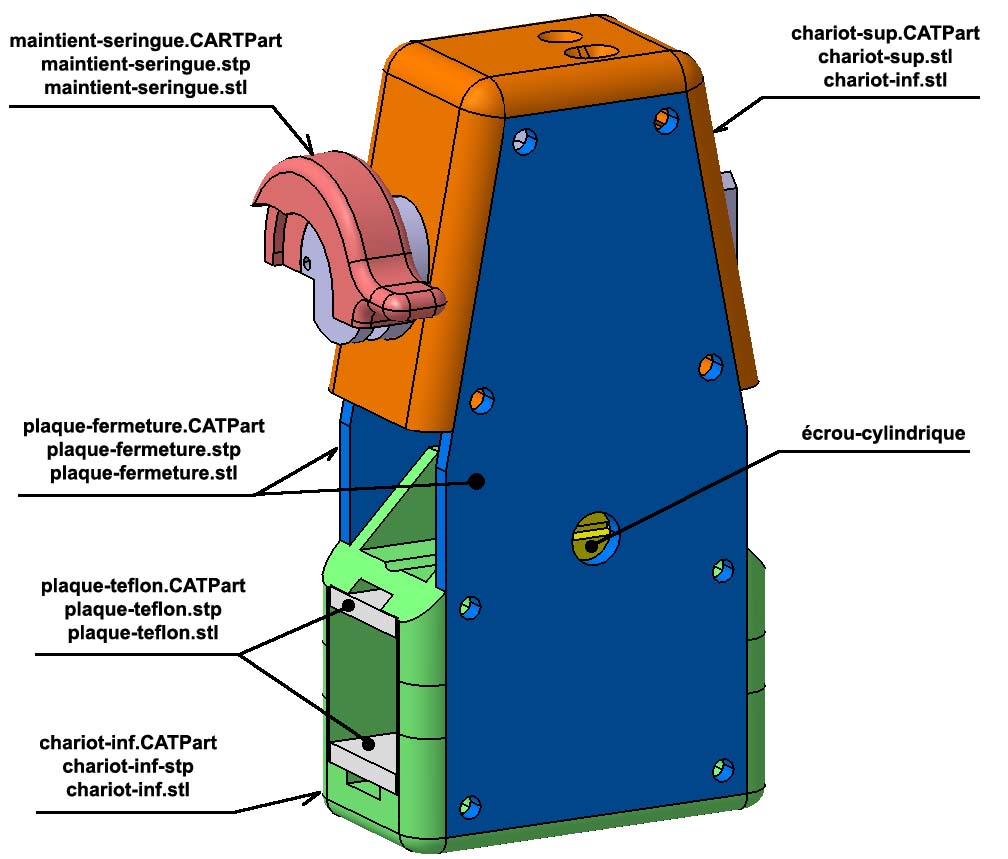
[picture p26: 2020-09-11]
carter et chassis/trolley/chariot-switch/assemblage.jpg

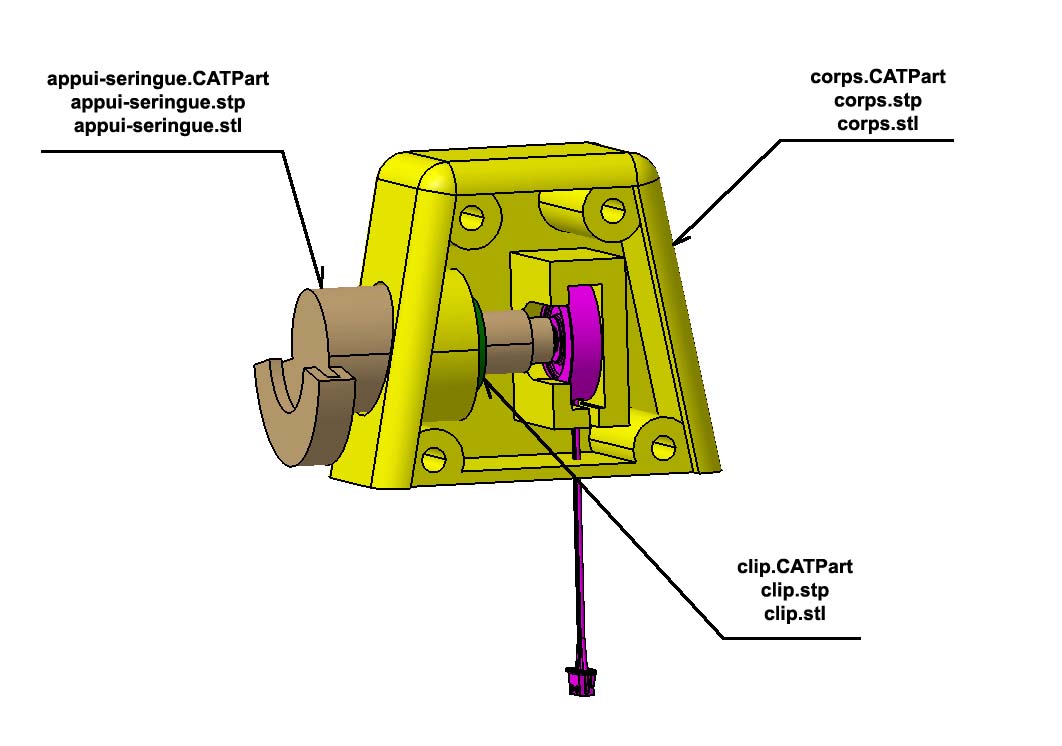
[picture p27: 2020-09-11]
carter et chassis/trolley/chariot-capteur-force/assemblage.jpg
